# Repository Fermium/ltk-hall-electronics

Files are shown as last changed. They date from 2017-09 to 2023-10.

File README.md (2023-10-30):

# Free Open Scientific Equipment

Fermium LTD announces the free release of all scientific equipment designs under the terms of the MIT license. You are free to use them as you wish.

## Why?

Our small business is no longer competitive in this sector, and thus we've ceased production of this scientific equipment.

## What's Included

- Microwave Optics Kit:
  - [Microwave RX and TX](https://github.com/Fermium/ltk-mw-electronic): A pair of ultra-low-cost 10GHz microwave transmitters and receivers
  - [Microwave Kit Display](https://github.com/Fermium/frm-mw-display)
  - [Diode Detector](https://github.com/Fermium/frm-mw-diode-detector): A 10GHz diode detector for studying evanescent waves and wave propagation in waveguides
  - [Mechanics](https://github.com/Fermium/ltk-mw-mechanics) including:
    - [Transmitter and Receiver](https://github.com/Fermium/ltk-mw-mechanics/tree/master/transmitter%20and%20receiver) with rear protractor
    - [Structure](https://github.com/Fermium/ltk-mw-mechanics/tree/master/structure) with feet, rulers, center protractor, and center mount
    - [PCB Optics Components](https://github.com/Fermium/ltk-mw-mechanics/tree/master/pcbs): Mirrors, polarizers, photon-sieves, Fresnel zone plates
    - [Waveguides](https://github.com/Fermium/ltk-mw-mechanics/tree/master/accessories/waveguides)

- Hall Effect Apparatus:
  - [Electronics](https://github.com/Fermium/ltk-hall-electronics) for the 2015, 2017, and 2019 models
  - [2015 Firmware](https://github.com/Fermium/Hall-firmware)
  - [2017 Firmware](https://github.com/Fermium/hall-firmware-v2#hall-effect-apparatus-firmware---2017)

# Hall effect apparatus electronics

This repository contains the electronics for the Hall effect apparatus. The electronics are designed in Altium Designer.

The manual can be found [here](https://github.com/Fermium/hall-effect-handbook).

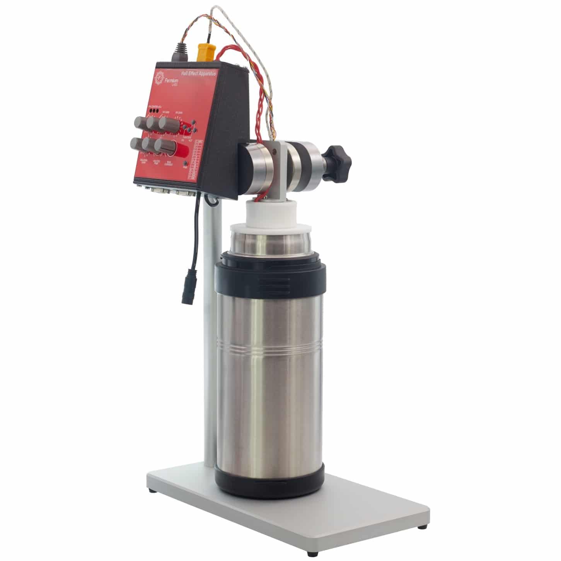
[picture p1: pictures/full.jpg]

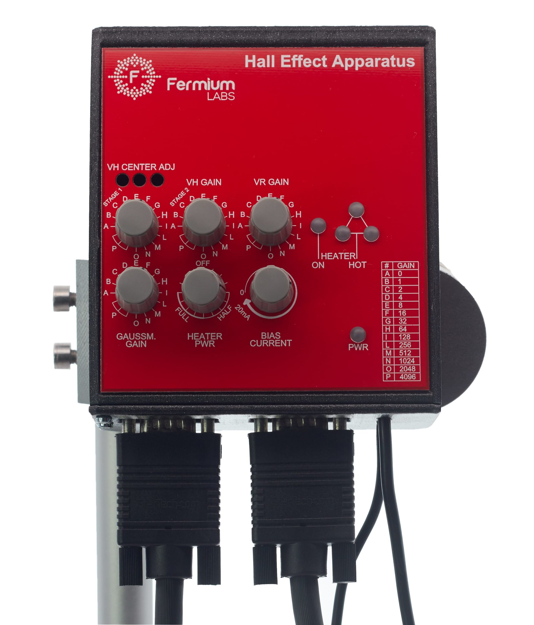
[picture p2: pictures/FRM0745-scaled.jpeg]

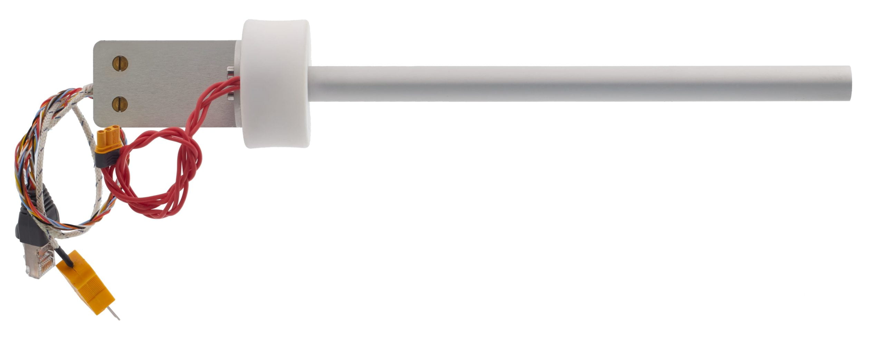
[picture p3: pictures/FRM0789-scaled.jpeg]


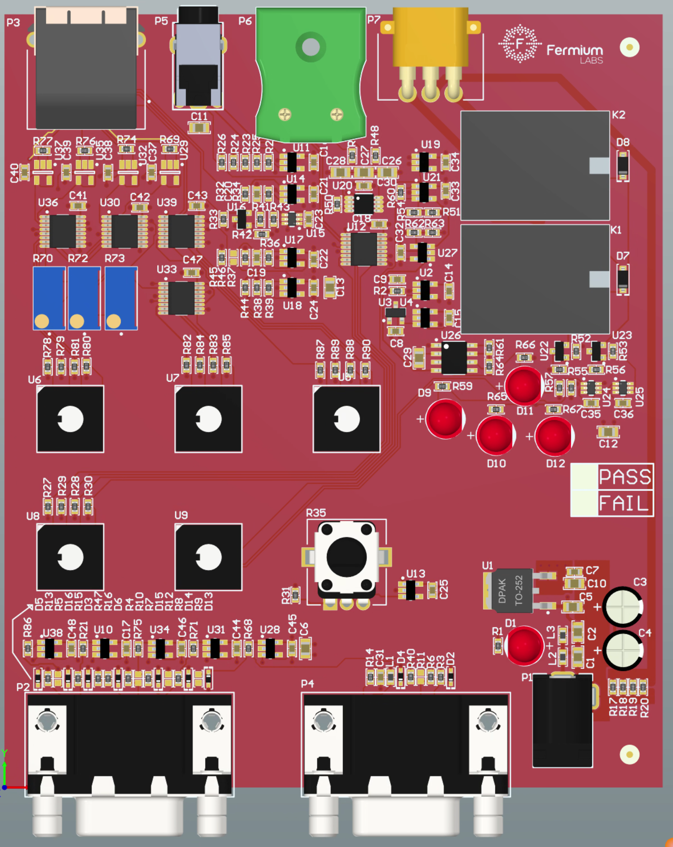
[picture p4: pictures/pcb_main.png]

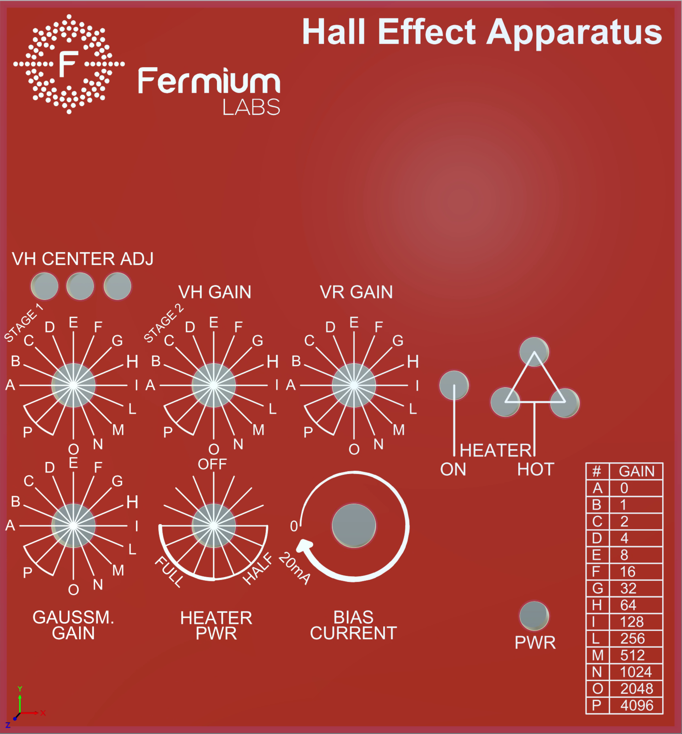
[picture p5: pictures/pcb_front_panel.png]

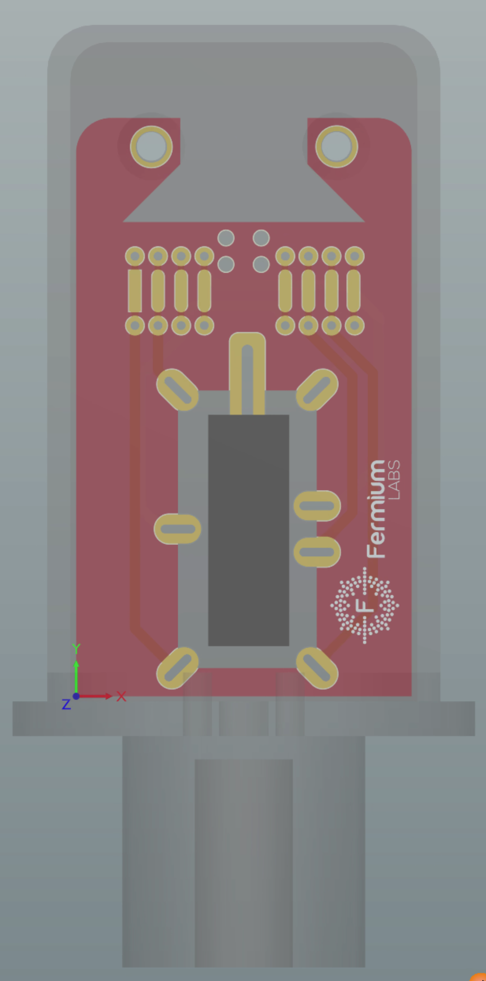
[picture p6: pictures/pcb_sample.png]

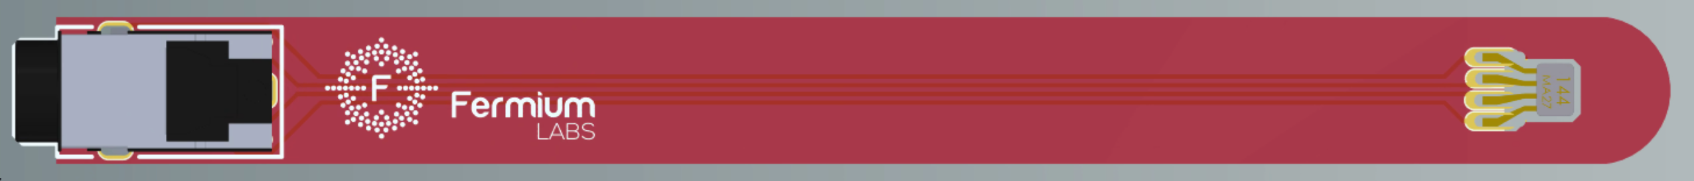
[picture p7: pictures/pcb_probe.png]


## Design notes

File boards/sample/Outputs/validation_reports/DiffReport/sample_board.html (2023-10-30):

Altium

# Differences Report for Project sample_board.PrjPcb and sample_board.PcbDoc

Date: | | 10/30/2023
Time: | | 4:42:38 PM
Filename: | | C:\Users\Shadow\Desktop\Repos\ltk-hall-electronics\exports\sample\validation_reports\DiffReport\sample_board.html

## Extra Room Definitions

Schematic Object | PCB Object
[Room sample_board (Scope=InComponentClass('sample_board')) TopLayer]

Back to top

## Different Comments

Schematic Object | PCB Object
Ge-P type [U1] | Sample [U1]

Back to top

## Different Types

Schematic Object | PCB Object
[logo] | [logo]
[P1] | [P1]

Back to top

## Changed Net Names

Schematic Object | PCB Object
[SAMPLE-I_N] | [NetP1_8]

Back to top

## Different Component Parameters

Schematic Object | PCB Object
[P1] | [P1]
[U1] | [U1]

Back to top

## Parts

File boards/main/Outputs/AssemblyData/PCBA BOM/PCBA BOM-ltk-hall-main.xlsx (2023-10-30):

Line # | Quantity | Bom Notes | Description | Designator | Layer | Manufacturer 1 | Manufacturer Part Number 1 | Manufacturer 2 | Manufacturer Part Number 2 | Manufacturer 3 | Manufacturer Part Number 3 | Manufacturer 4 | Manufacturer Part Number 4 | Manufacturer 5 | Manufacturer Part Number 5 | S 1 | SPN 1 | S 2 | SPN 2 | S 3 | SPN 3 | S 4 | SPN 4 | S 5 | SPN 5 | S 6 | SPN 6 | S 7 | SPN 7 | S 8 | SPN 8
1 | 2 |  | CAP THT ELEC 220uF 25V 20% | C3, C4 |  | Rubycon | 25PK220MEFC-6.3*11 |  |  |  |  |  |  |  |  | LCSC | C109337
2 | 2 |  | CAP SMD MLCC 10nF 50V 0603 X7R | C19, C20 |  | Yageo | CC0603KRX7R9BB103 | Samsung Electro-Mechanics | CL10B103KB8NFNC | Yageo | CC0603JRX7R9BB103 |  |  |  |  | LCSC | C307477 | LCSC | C100042
3 | 4 |  | CAP SMD MLCC 10uF 25V 0805 X5R | C26, C27, C28, C29 |  | Samsung Electro-Mechanics | CL21A106KAYNNNE | Murata | GRM21BR61E106KA73L |  |  |  |  |  |  | LCSC | C84416 | LCSC | C15850
4 | 8 |  | CAP SMD MLCC 22uF 25V 0805 X5R | C1, C2, C5, C6, C10, C11, C12, C13 |  | Samsung Electro-Mechanics | CL21A106KAYNNNE | Murata | GRM21BR61E106KA73L |  |  |  |  |  |  | LCSC | C84416 | LCSC | C15850
5 | 32 |  | CAP SMD MLCC 100nF 25V 0603 X7R | C7, C8, C9, C14, C15, C16, C17, C18, C21, C22, C23, C24, C25, C30, C31, C32, C33, C34, C35, C36, C37, C38, C39, C40, C41, C42, C43, C44, C45, C46, C47, C48 |  | Samsung Electro-Mechanics | CL10B104KA8NNNC | Yageo | CC0603KRX7R9BB104 |  |  |  |  |  |  | LCSC | C1590 | LCSC | C14663
6 | 1 |  | CONN DC 3 POLE 15A PCB MALE | P7 |  | Changzhou Amass Elec | MR30PW-M |  |  |  |  |  |  |  |  | TME | MR30PW-M
7 | 2 |  | CONN D-SUB HD 15POLES BLACK THT | P2, P4 |  | FCI | ICD15S13E4GV00LF |  |  |  |  |  |  |  |  | TME | ICD15S13E4GV00LF
8 | 1 |  | CONN JACK 3.5MM 4POLE THT | P5 |  | Cliff | FC68125 |  |  |  |  |  |  |  |  | TME | FC68125
9 | 1 |  | CONN RJ45 SHIELDED | P3 |  | TE Connectivity | 5555153-1 |  |  |  |  |  |  |  |  | LCSC | C125072
10 | 1 |  | CONN THERMOCOUPLE K-TYPE THT | P6 |  | Labfacility | IM-K-PCB |  |  |  |  |  |  |  |  | Farnell | 3810628
11 | 1 |  | CONN THT DC JACK 0.5A 30VDC 5Kcycles | P1 |  | HRO Electronics | DC-005A-20A |  |  |  |  |  |  |  |  | LCSC | C191049
12 | 5 |  | DIODE LED THT 5MM RED 200mcd | D1, D9, D10, D11, D12 |  | Everlight | 333-2SURD/S530-A3-L |  |  |  |  |  |  |  |  | LCSC | C99758
13 | 2 |  | DIODE SMD 100V 150mA 1.5Vf SOD-123 4148 | D7, D8 |  | MCC | 1N4148W-TP |  |  |  |  |  |  |  |  | LCSC | C77978
14 | 9 |  | DIODE SMD TVS 5V BIDIRECTIONAL SOD-523 | D2, D3, D4, D5, D6, D13, D14, D15, D16 |  | Born Semiconductor | PESD5V0S1BBN | Nexperia | PESD5V0S1BB,115 |  |  |  |  |  |  | LCSC | C314264 | LCSC | C97640
15 | 3 |  | FER SMD CHIP 0603 800mA 1K@100MHz 300mOhm | L1, L2, L3 |  | TDK | MPZ1608S102ATA00 |  |  |  |  |  |  |  |  | LCSC | C76814
16 | 3 |  | IC LOGIC PORT CONFIGURABLE AND, OR, NAND, NOR, XOR, BUFFER, NOT 8ns 74XX58 SC-70 | U15, U24, U25 |  | ON Semiconductor | NC7SZ58P6X | Texas Instruments | SN74LVC1G58DCKR |  |  |  |  |  |  | LCSC | C232804 | LCSC | C7842
17 | 19 |  | IC OPAMP 65uV 1pA RRIO 5V 80mA SOT-23-5 | U2, U4, U10, U11, U13, U14, U17, U18, U19, U21, U27, U28, U29, U31, U32, U34, U35, U37, U38 |  | Analog Devices | AD8605ARTZ |  |  |  |  |  |  |  |  | LCSC | C9641
18 | 5 |  | IC PGA G0-4094 SPI-PARALLEL 5V RRIO SSOP-16 | U12, U30, U33, U36, U39 |  | Analog Devices | LTC6915CGN#PBF |  |  |  |  |  |  |  |  | Mouser | 584-LTC6915CGN#PBF
19 | 1 |  | IC SMD LINEAR VOLTAGE REGULATOR 5V 500mA DPAK/TO-252 | U1 |  | ST Microelectronics | L78M05ABDT-TR |  |  |  |  |  |  |  |  | LCSC | C58069
20 | 1 |  | IC SMD TIMER NE555 SOIC-8 | U26 |  | Texas Instruments | NE555DR |  |  |  |  |  |  |  |  | LCSC | C7593
21 | 1 |  | IC THERMOCOUPLE AMPLIFIER MSOP-8 | U20 |  | Analog Devices | AD8495ARMZ-R7 |  |  |  |  |  |  |  |  | LCSC | C59658
22 | 1 |  | IC VOLTAGE REF SERIES 2.5V 75ppm 0.2% SOT-23 | U3 |  | Texas Instruments | REF3025AIDBZR |  |  |  |  |  |  |  |  | LCSC | C11334
23 | 3 |  | MOSFET N-CHANNEL LOGIC LEVEL 300mA 3ohm 60V ESD-PROT 2N7002K SOT-23 | U16, U22, U23 |  | ON Semiconductor | 2N7002KT1G | Vishay | 2N7002K-T1-GE3 | Diodes Inc. | 2N7002K-7 |  |  |  |  | LCSC | C81445 | LCSC | C116584 | LCSC | C85047
24 | 1 |  | POT 10K 20% SHAFT 6mmx7.4mm LIN | R35 |  | ALPS | RK09K1130A6S |  |  |  |  |  |  |  |  | LCSC | C209770
25 | 1 |  | POT TRIMMER LINEAR 10K 25TURNS VERT THT | R72 |  | Bourns | 3296W-1-103LF |  |  |  |  |  |  |  |  | LCSC | C34846
26 | 2 |  | POT TRIMMER LINEAR 50K 25TURNS VERT THT | R70, R73 |  | Bourns | 3296W-1-503LF |  |  |  |  |  |  |  |  | LCSC | C83686
27 | 2 |  | RELAY SPDT 10A 250VAC 12VDC SUBMINIATURE | K1, K2 |  | Omron | G5LE-14-DC12 |  |  |  |  |  |  |  |  | LCSC | C116964
28 | 24 |  | RES SMD 0 OHM 5% 1/10W 0603 | R4, R5, R6, R7, R8, R9, R10, R11, R12, R13, R14, R15, R16, R17, R18, R19, R20, R31, R32, R46, R69, R74, R76, R77 |  | Yageo | RC0603JR-070RL | Uniroyal | 0603WAF0000T5E |  |  |  |  |  |  | LCSC | C95177 | LCSC | C21189
29 | 6 |  | RES SMD 1K OHM 1% 1/10W 0603 | R2, R22, R25, R37, R38, R40 |  | Yageo | RC0603FR-071KL | Uniroyal | 0603WAF1001T5E |  |  |  |  |  |  | LCSC | C21190 | LCSC | C22548
30 | 1 |  | RES SMD 1M OHM 1% 1/10W 0603 | R50 |  | Yageo | RC0603FR-071ML | Uniroyal | 0603WAF1004T5E |  |  |  |  |  |  | LCSC | C105578 | LCSC | C22935
31 | 1 |  | RES SMD 1.2K OHM 1% 1/10W 0603 | R62 |  | Yageo | RC0603FR-071K2L | Uniroyal | 0603WAF1201T5E |  |  |  |  |  |  | LCSC | C114605 | LCSC | C22765
32 | 1 |  | RES SMD 1.5K OHM 1% 1/10W 0603 | R63 |  | Yageo | RC0603FR-071K5L | Uniroyal | 0603WAF1501T5E |  |  |  |  |  |  | LCSC | C22843 | LCSC | C114668
33 | 1 |  | RES SMD 3.3K OHM 1% 1/10W 0603 | R51 |  | Yageo | RC0603FR-073K3L | Uniroyal | 0603WAF3301T5E |  |  |  |  |  |  | LCSC | C108078 | LCSC | C22978
34 | 1 |  | RES SMD 5.6K OHM 1% 1/10W 0603 | R54 |  | Yageo | RC0603FR-075K6L | Uniroyal | 0603WAF5601T5E |  |  |  |  |  |  | LCSC | C23189 | LCSC | C114627
35 | 1 |  | RES SMD 10 OHM 0.1% 1/16W 25ppm 0603 | R45 |  | Uniroyal | TC0325B100JT5E | Viking Tech | AR03BTCX0100 |  |  |  |  |  |  | LCSC | C319923 | LCSC | C146565
36 | 29 |  | RES SMD 10K OHM 1% 1/10W 0603 | R27, R28, R29, R30, R33, R34, R36, R42, R43, R48, R49, R55, R56, R57, R58, R61, R64, R78, R79, R80, R81, R82, R83, R84, R85, R87, R88, R89, R90 |  | Yageo | RC0603FR-0710KL | Uniroyal | 0603WAF1002T5E |  |  |  |  |  |  | LCSC | C98220 | LCSC | C25804
37 | 1 |  | RES SMD 24K OHM 1% 1/10W 0603 | R39 |  | Yageo | RC0603FR-0724KL |  |  |  |  |  |  |  |  | LCSC | C137760
38 | 1 |  | RES SMD 39K OHM 1% 1/10W 0603 | R60 |  | Yageo | RC0603FR-0739KL | Uniroyal | 0603WAF3902T5E |  |  |  |  |  |  | LCSC | C23153 | LCSC | C163424
39 | 16 |  | RES SMD 100 OHM 1% 1/10W 0603 | R3, R21, R23, R24, R41, R44, R47, R52, R53, R65, R66, R67, R68, R71, R75, R86 |  | Yageo | RC0603FR-07100RL | Uniroyal | 0603WAF1000T5E |  |  |  |  |  |  | LCSC | C105588 | LCSC | C22775
40 | 2 |  | RES SMD 330 OHM 1% 1/10W 0603 | R1, R59 |  | Yageo | RC0603FR-07330RL | Uniroyal | 0603WAF3300T5E |  |  |  |  |  |  | LCSC | C105881 | LCSC | C23138
41 | 1 |  | RES SMD 499 OHM 1% 1/10W 0603 | R26 |  | Yageo | RC0603FR-07499RL | Uniroyal | 0603WAF4990T5E |  |  |  |  |  |  | LCSC | C23065
42 | 5 |  | SWITCH ROTARY HEX/BCD 16 POSITIONS | U5, U6, U7, U8, U9 |  | Omron | A6R-162RS |  |  |  |  |  |  |  |  | TME | A6R-162RS

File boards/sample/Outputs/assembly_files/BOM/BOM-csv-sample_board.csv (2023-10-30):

Supplier Part Number 1 | Quantity | Comment | Footprint | Supplier 1 | Pads | Designator
ge-p-sample | 1 | Ge-P type | Germanium Sample | Changsha Santech Materials | N/A | U1

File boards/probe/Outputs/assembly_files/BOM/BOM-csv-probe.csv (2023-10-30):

Supplier Part Number 1 | Quantity | Manufacturer Part Number | Comment | Footprint | Supplier 1 | Designator | Pads | Manufacturer
FC68125 | 1 | FC68125 |  | FC68125 | TME | P1 | 5 THT | CLIFF
HE144P | 1 | HE144P |  | HE144P-buried | Asensor | U1 | 4 THT | Asensor

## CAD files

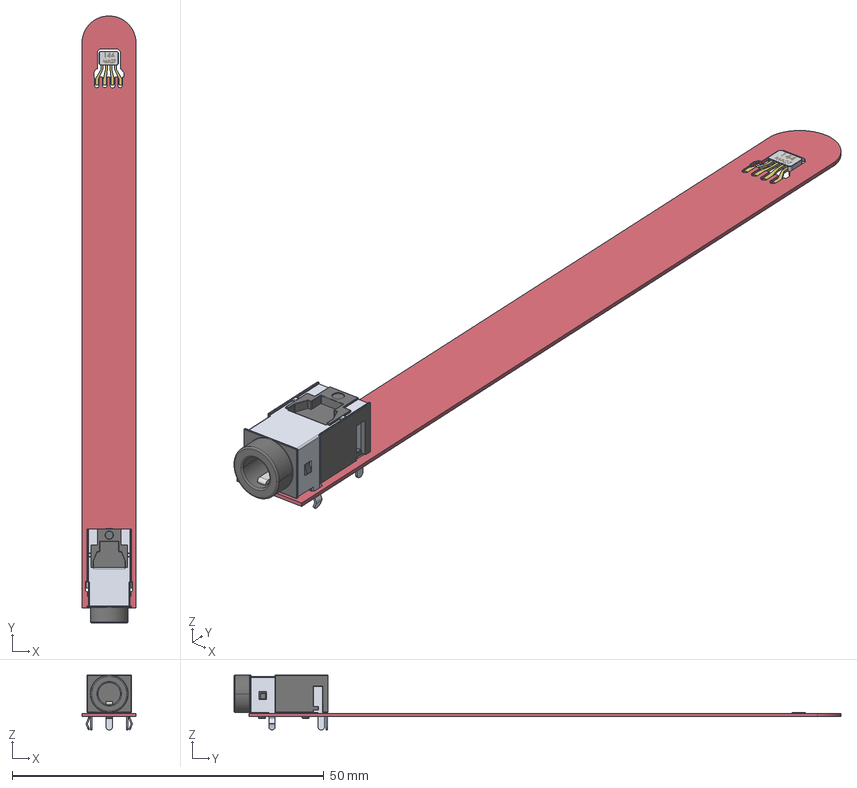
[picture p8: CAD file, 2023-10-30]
boards/probe/Outputs/assembly_files/ExportSTEP/probe.step
8.60 x 97.4 x 8.80 mm
short
FC68125

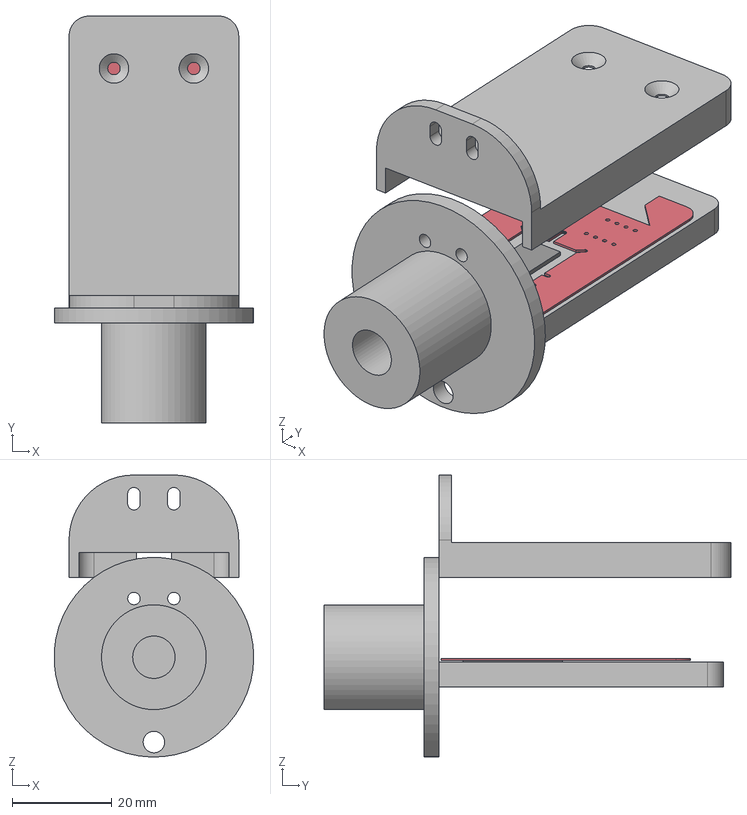
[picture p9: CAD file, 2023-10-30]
boards/sample/Outputs/assembly_files/ExportSTEP/sample_board.step
40.0 x 81.5 x 56.5 mm
Extruded
COPERCHIO_RGB8421504

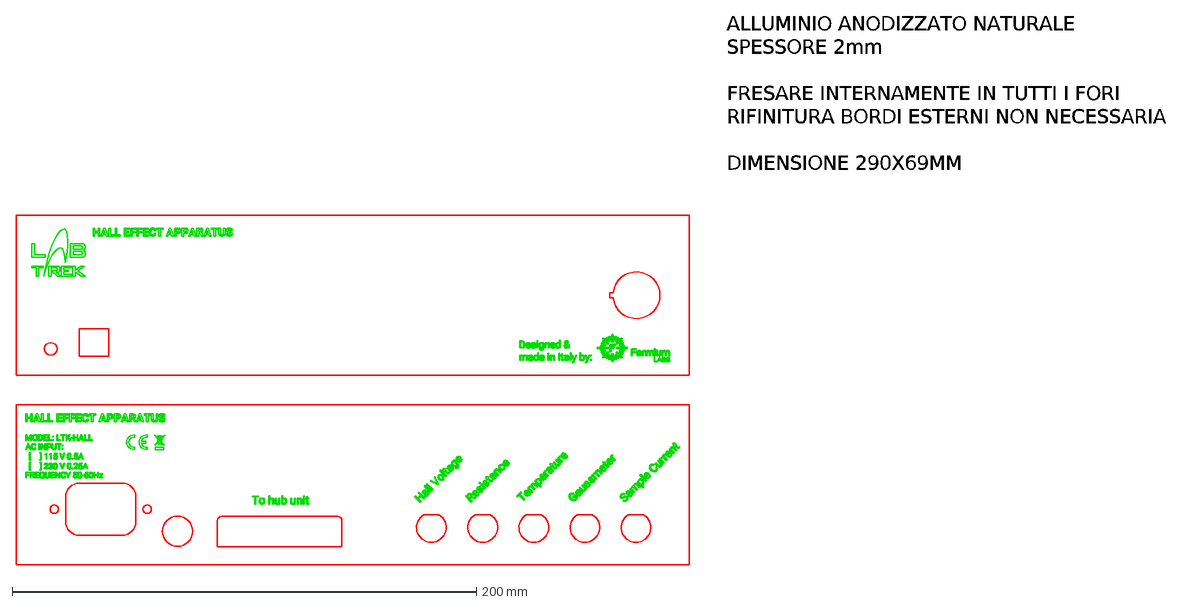
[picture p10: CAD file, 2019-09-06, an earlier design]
mechanical_OLD/front panels/main/main_definitivo_clean_dxf_2000.dxf
ALLUMINIO ANODIZZATO NATURALE SPESSORE 2mm FRESARE INTERNAMENTE IN TUTTI I FORI RIFINITURA BORDI ESTERNI NON NECESSARIA DIMENSIONE 290X69MM

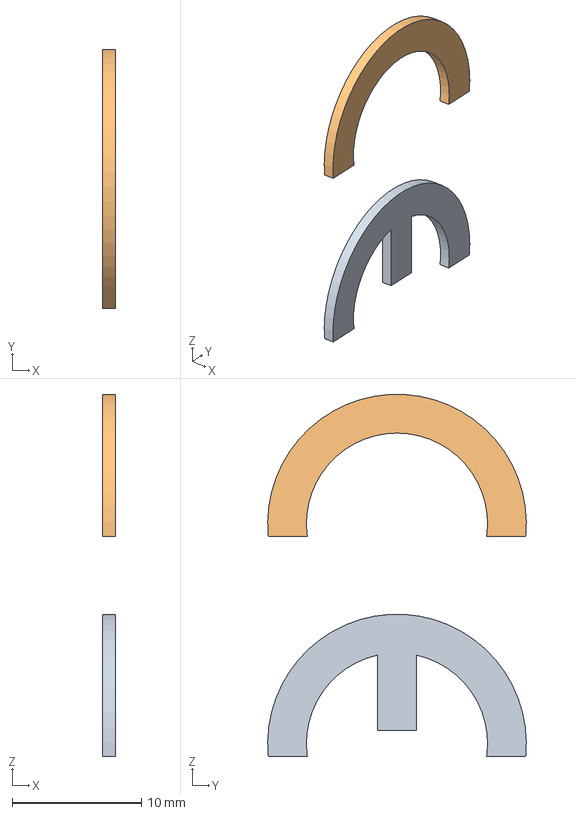
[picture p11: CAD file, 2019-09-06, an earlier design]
mechanical_OLD/front panels/components docs/ce-logo.snapshot.3/ce-logo.stp
1.00 x 20.0 x 28.0 mm

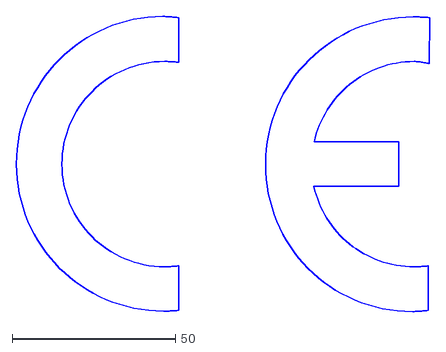
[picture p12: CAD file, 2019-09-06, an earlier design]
mechanical_OLD/front panels/components docs/CE_LOGO/CE_logo.dxf
126.5 x 90.3

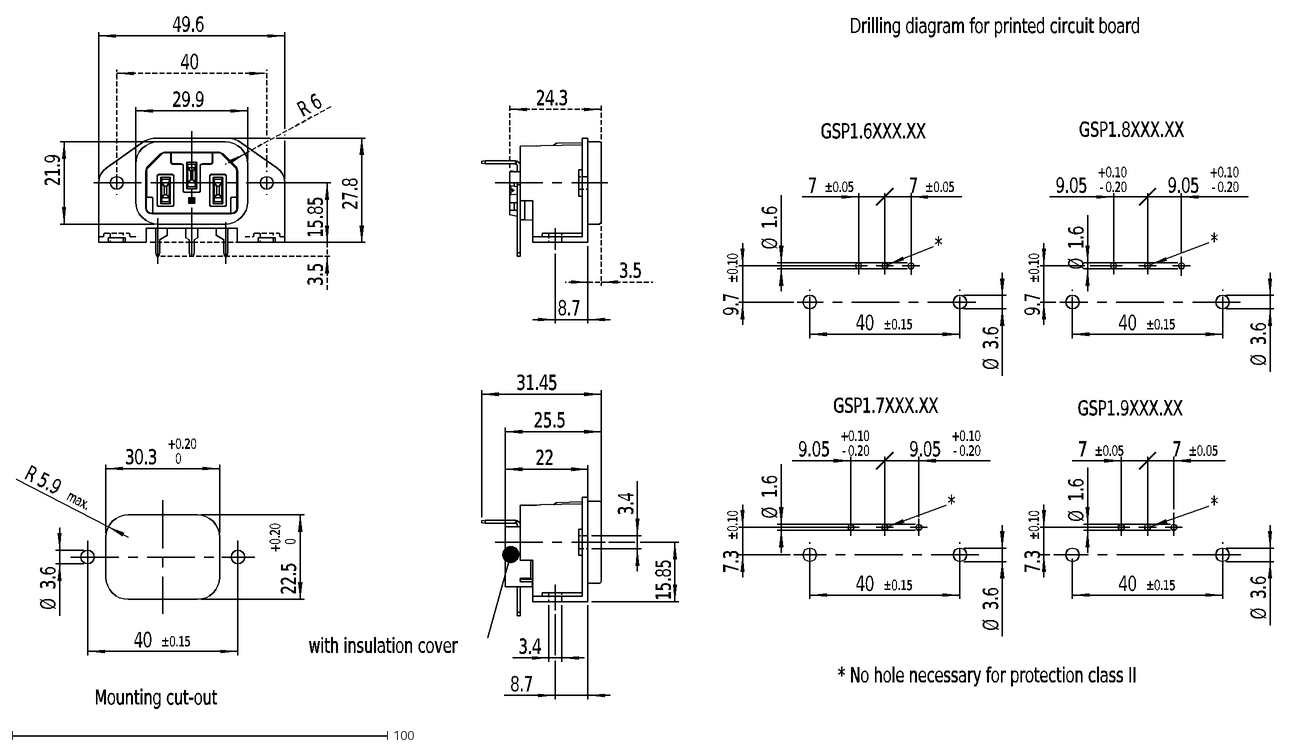
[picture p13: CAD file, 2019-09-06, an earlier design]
mechanical_OLD/front panels/components docs/e_0105.1305_2.1e001.dxf
3.5
15.85
29.9
21.9
27.8
49.6
40
R
6
8.7
24.3
25.5
22
31.45
3.4
with insulation cover
Ø
1.6
9.05
-
0.20
+
0.10
7
±0.05
7.3
±0.10
9.7
3.6
±0.15
Drilling diagram for printed circuit board
*
* No hole necessary for protection class II
GSP1.6XXX.XX
GSP1.7XXX.XX
GSP1.8XXX.XX
GSP1.9XXX.XX
30.3
0
22.5
5.9
max.
Mounting cut-out

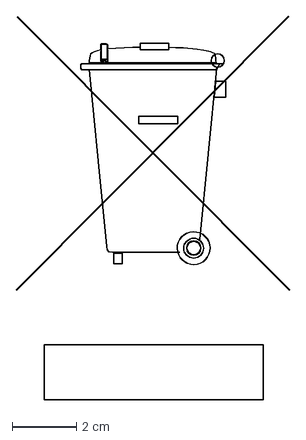
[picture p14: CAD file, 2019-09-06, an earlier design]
mechanical_OLD/front panels/components docs/WHEELIE_BIN_LOGO/Wheeled_bin.dxf
8.55 x 12.0 cm

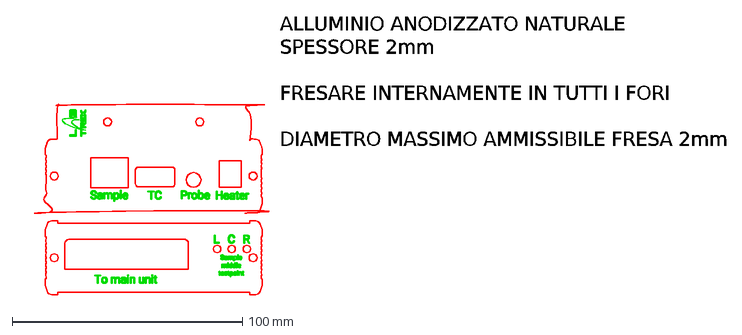
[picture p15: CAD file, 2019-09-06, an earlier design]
mechanical_OLD/front panels/hub/hub_definitivo_clean_dxf_2000.dxf
ALLUMINIO ANODIZZATO NATURALE SPESSORE 2mm FRESARE INTERNAMENTE IN TUTTI I FORI DIAMETRO MASSIMO AMMISSIBILE FRESA 2mm

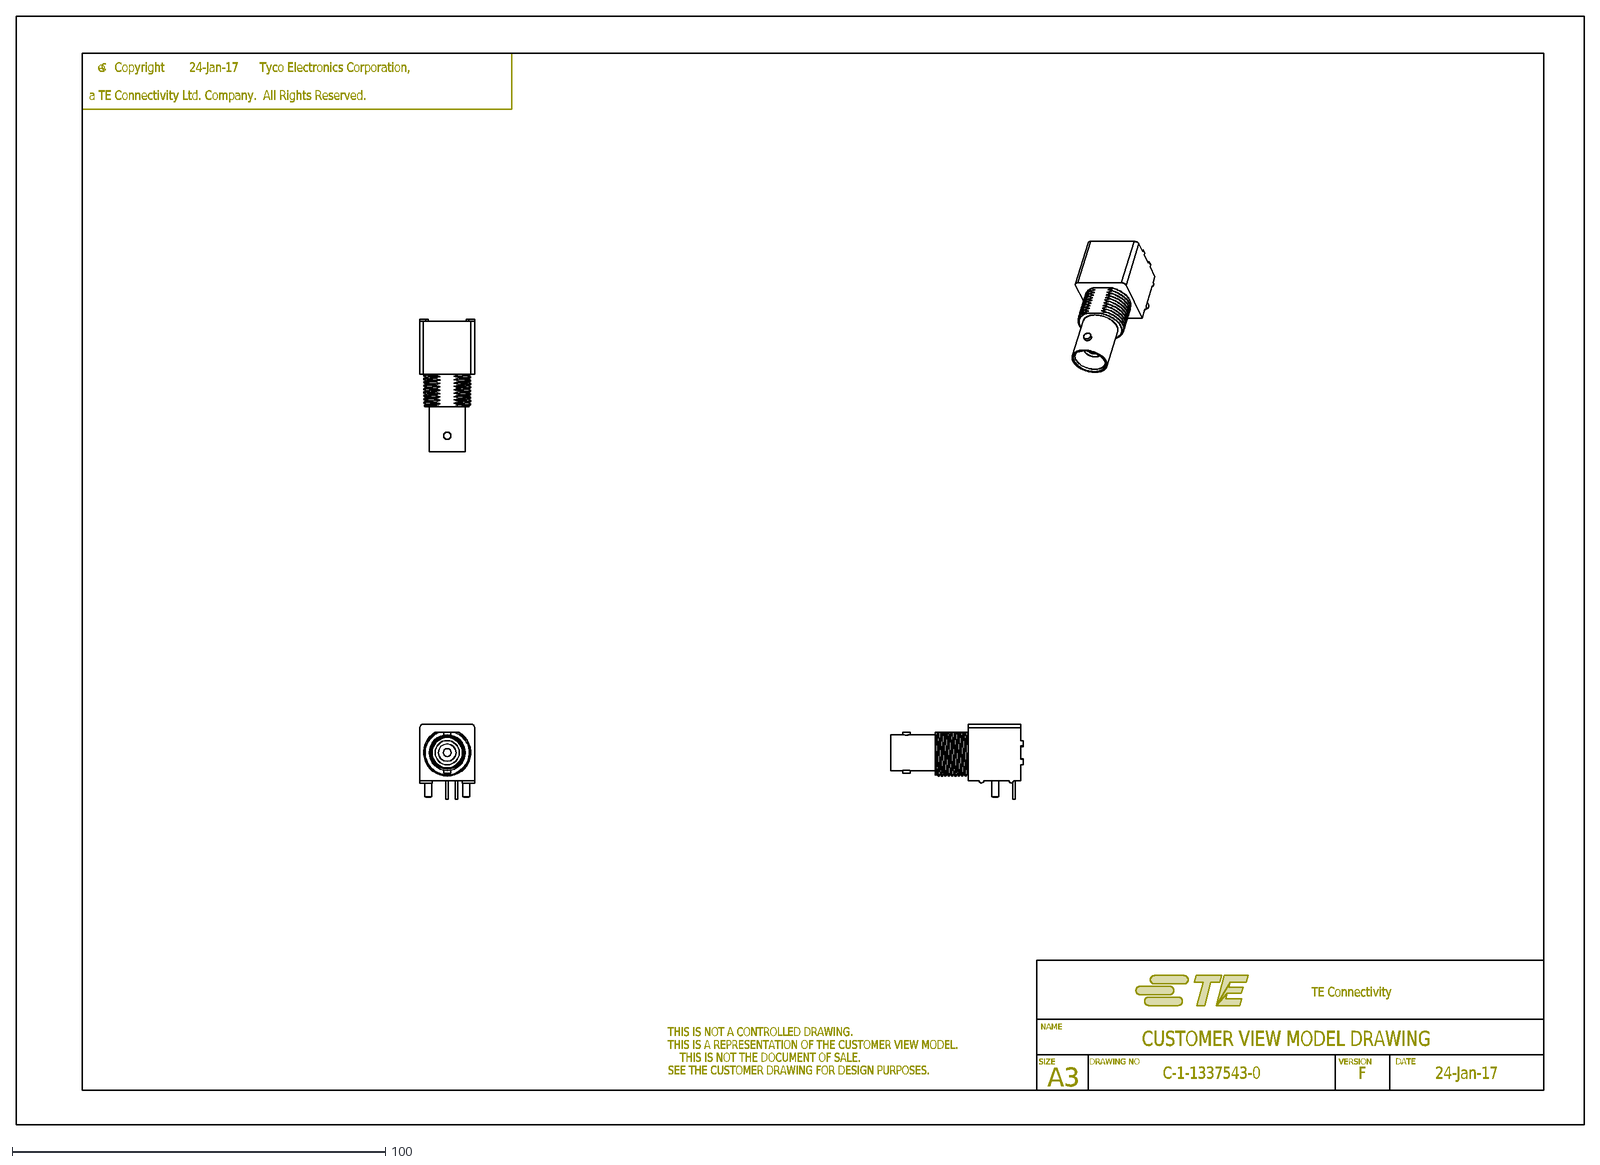
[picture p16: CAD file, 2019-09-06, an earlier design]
mechanical_OLD/front panels/components docs/c-1-1337543-0-f-2d.dxf
SIZE
DRAWING NO
VERSION
NAME
A3
CUSTOMER VIEW MODEL DRAWING
TE Connectivity
DATE
THIS IS NOT A CONTROLLED DRAWING.
THIS IS A REPRESENTATION OF THE CUSTOMER VIEW MODEL.
THIS IS NOT THE DOCUMENT OF SALE.
SEE THE CUSTOMER DRAWING FOR DESIGN PURPOSES.
c
C-1-1337543-0
F
24-Jan-17
Copyright
Tyco Electronics Corporation,
a TE Connectivity Ltd. Company. All Rights Reserved.

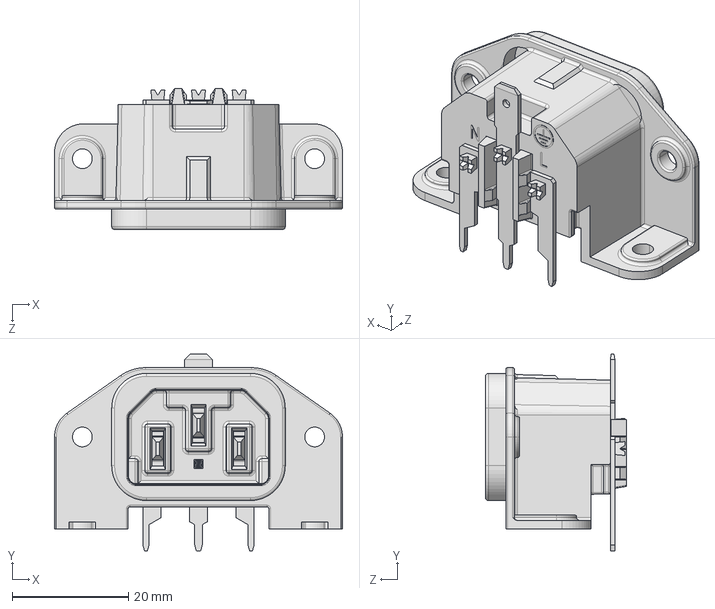
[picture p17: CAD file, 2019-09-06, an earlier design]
mechanical_OLD/front panels/components docs/e_0100.2041d007.step
49.6 x 33.9 x 24.3 mm

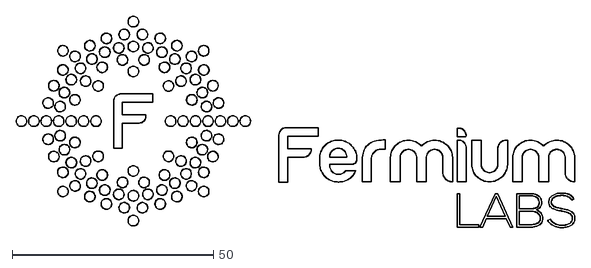
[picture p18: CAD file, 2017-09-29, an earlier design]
mechanical_OLD/front panels/components docs/Horizontal-Black.dxf
138.9 x 52.5

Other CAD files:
boards/main/Outputs/AssemblyData/AutoCAD dwg_dxf File PCB/ltk-hall-main.DWG
boards/main/Outputs/DevMechanicalData/ltk-hall-main.DWG
boards/probe/Outputs/assembly_files/AutoCAD PCB/probe.DWG
boards/sample/Outputs/assembly_files/AutoCAD PCB/sample_board.DWG
mechanical_OLD/front panels/main/main.dwg
mechanical_OLD/front panels/hub/Hub.dwg
mechanical_OLD/front panels/components docs/labtrek-logo.dwg
mechanical_OLD/front panels/components docs/Hub.dwg
mechanical_OLD/front panels/components docs/WHEELIE_BIN_LOGO/Wheeled_bin.dwg

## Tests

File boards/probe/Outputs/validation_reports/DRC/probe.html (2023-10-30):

Altium

# Design Rule Verification Report

Date: | | 10/30/2023
Time: | | 4:41:53 PM
Elapsed Time: | | 00:00:01
Filename: | | C:\Users\Shadow\Desktop\Repos\ltk-hall-electronics\boards\probe\probe.PcbDoc

Warnings: | | 0
Rule Violations: | | 34

## Summary

Warnings | Count
Total | 0

Rule Violations | Count
Clearance Constraint (Gap=6mil) (All),(All) | 12
Short-Circuit Constraint (Allowed=No) (All),(All) | 13
Un-Routed Net Constraint ( (All) ) | 0
Modified Polygon (Allow modified: No), (Allow shelved: No) | 0
Width Constraint (Min=6mil) (Max=200mil) (Preferred=10mil) (All) | 0
Power Plane Connect Rule(Relief Connect )(Expansion=20mil) (Conductor Width=10mil) (Air Gap=10mil) (Entries=4) (All) | 0
Hole Size Constraint (Min=11.811mil) (Max=100mil) (All) | 4
Hole To Hole Clearance (Gap=10mil) (All),(All) | 0
Minimum Solder Mask Sliver (Gap=10mil) (All),(All) | 3
Silk To Solder Mask (Clearance=10mil) (IsPad),(All) | 2
Silk to Silk (Clearance=10mil) (All),(All) | 0
Net Antennae (Tolerance=0mil) (All) | 0
Height Constraint (Min=0mil) (Max=1000mil) (Prefered=500mil) (All) | 0
Total | 34

Clearance Constraint (Gap=6mil) (All),(All)

Clearance Constraint: (Collision < 6mil) Between Board Cutout (Multi-Layer)Region (0 hole(s)) Multi-Layer And Pad U1-1(302.724mil,3542.307mil) on Multi-Layer

Clearance Constraint: (Collision < 6mil) Between Board Cutout (Multi-Layer)Region (0 hole(s)) Multi-Layer And Pad U1-1(302.724mil,3542.307mil) on Multi-Layer

Clearance Constraint: (Collision < 6mil) Between Board Cutout (Multi-Layer)Region (0 hole(s)) Multi-Layer And Pad U1-2(254.724mil,3541.307mil) on Multi-Layer

Clearance Constraint: (Collision < 6mil) Between Board Cutout (Multi-Layer)Region (0 hole(s)) Multi-Layer And Pad U1-2(254.724mil,3541.307mil) on Multi-Layer

Clearance Constraint: (Collision < 6mil) Between Board Cutout (Multi-Layer)Region (0 hole(s)) Multi-Layer And Pad U1-3(204.724mil,3543.307mil) on Multi-Layer

Clearance Constraint: (Collision < 6mil) Between Board Cutout (Multi-Layer)Region (0 hole(s)) Multi-Layer And Pad U1-3(204.724mil,3543.307mil) on Multi-Layer

Clearance Constraint: (Collision < 6mil) Between Board Cutout (Multi-Layer)Region (0 hole(s)) Multi-Layer And Pad U1-4(155.724mil,3542.307mil) on Multi-Layer

Clearance Constraint: (Collision < 6mil) Between Board Cutout (Multi-Layer)Region (0 hole(s)) Multi-Layer And Pad U1-4(155.724mil,3542.307mil) on Multi-Layer

Clearance Constraint: (Collision < 6mil) Between Board Cutout (Multi-Layer)Region (0 hole(s)) Multi-Layer And Track (157.48mil,3456.693mil)(157.48mil,3602.132mil) on Top Layer

Clearance Constraint: (Collision < 6mil) Between Board Cutout (Multi-Layer)Region (0 hole(s)) Multi-Layer And Track (157.48mil,3456.693mil)(157.48mil,3602.132mil) on Top Layer

Clearance Constraint: (Collision < 6mil) Between Board Cutout (Multi-Layer)Region (0 hole(s)) Multi-Layer And Track (303.15mil,3456.693mil)(303.15mil,3598.95mil) on Top Layer

Clearance Constraint: (Collision < 6mil) Between Board Cutout (Multi-Layer)Region (0 hole(s)) Multi-Layer And Track (303.15mil,3456.693mil)(303.15mil,3598.95mil) on Top Layer

Back to top

Short-Circuit Constraint (Allowed=No) (All),(All)

Short-Circuit Constraint: Between Board Cutout (Multi-Layer)Region (0 hole(s)) Multi-Layer And Board Cutout (Multi-Layer)Region (0 hole(s)) Multi-Layer Location : [X = 4680.685mil][Y = 5609.394mil]

Short-Circuit Constraint: Between Board Cutout (Multi-Layer)Region (0 hole(s)) Multi-Layer And Pad U1-1(302.724mil,3542.307mil) on Multi-Layer Location : [X = 4751.543mil][Y = 5545.398mil]

Short-Circuit Constraint: Between Board Cutout (Multi-Layer)Region (0 hole(s)) Multi-Layer And Pad U1-1(302.724mil,3542.307mil) on Multi-Layer Location : [X = 4751.543mil][Y = 5545.398mil]

Short-Circuit Constraint: Between Board Cutout (Multi-Layer)Region (0 hole(s)) Multi-Layer And Pad U1-2(254.724mil,3541.307mil) on Multi-Layer Location : [X = 4703.543mil][Y = 5544.874mil]

Short-Circuit Constraint: Between Board Cutout (Multi-Layer)Region (0 hole(s)) Multi-Layer And Pad U1-2(254.724mil,3541.307mil) on Multi-Layer Location : [X = 4703.543mil][Y = 5544.874mil]

Short-Circuit Constraint: Between Board Cutout (Multi-Layer)Region (0 hole(s)) Multi-Layer And Pad U1-3(204.724mil,3543.307mil) on Multi-Layer Location : [X = 4653.543mil][Y = 5545.874mil]

Short-Circuit Constraint: Between Board Cutout (Multi-Layer)Region (0 hole(s)) Multi-Layer And Pad U1-3(204.724mil,3543.307mil) on Multi-Layer Location : [X = 4653.543mil][Y = 5545.874mil]

Short-Circuit Constraint: Between Board Cutout (Multi-Layer)Region (0 hole(s)) Multi-Layer And Pad U1-4(155.724mil,3542.307mil) on Multi-Layer Location : [X = 4605.083mil][Y = 5545.214mil]

Short-Circuit Constraint: Between Board Cutout (Multi-Layer)Region (0 hole(s)) Multi-Layer And Pad U1-4(155.724mil,3542.307mil) on Multi-Layer Location : [X = 4605.083mil][Y = 5545.224mil]

Short-Circuit Constraint: Between Board Cutout (Multi-Layer)Region (0 hole(s)) Multi-Layer And Track (157.48mil,3456.693mil)(157.48mil,3602.132mil) on Top Layer Location : [X = 4606.299mil][Y = 5546.96mil]

Short-Circuit Constraint: Between Board Cutout (Multi-Layer)Region (0 hole(s)) Multi-Layer And Track (157.48mil,3456.693mil)(157.48mil,3602.132mil) on Top Layer Location : [X = 4606.299mil][Y = 5548.001mil]

Short-Circuit Constraint: Between Board Cutout (Multi-Layer)Region (0 hole(s)) Multi-Layer And Track (303.15mil,3456.693mil)(303.15mil,3598.95mil) on Top Layer Location : [X = 4751.968mil][Y = 5546.597mil]

Short-Circuit Constraint: Between Board Cutout (Multi-Layer)Region (0 hole(s)) Multi-Layer And Track (303.15mil,3456.693mil)(303.15mil,3598.95mil) on Top Layer Location : [X = 4751.968mil][Y = 5546.682mil]

Back to top

Hole Size Constraint (Min=11.811mil) (Max=100mil) (All)

Hole Size Constraint: (118.11mil > 100mil) Pad U1-1(302.724mil,3542.307mil) on Multi-Layer Actual Slot Hole Width = 118.11mil

Hole Size Constraint: (118.11mil > 100mil) Pad U1-2(254.724mil,3541.307mil) on Multi-Layer Actual Slot Hole Width = 118.11mil

Hole Size Constraint: (118.11mil > 100mil) Pad U1-3(204.724mil,3543.307mil) on Multi-Layer Actual Slot Hole Width = 118.11mil

Hole Size Constraint: (118.11mil > 100mil) Pad U1-4(155.724mil,3542.307mil) on Multi-Layer Actual Slot Hole Width = 118.11mil

Back to top

Minimum Solder Mask Sliver (Gap=10mil) (All),(All)

Minimum Solder Mask Sliver Constraint: (0.63mil < 10mil) Between Pad U1-1(302.724mil,3542.307mil) on Multi-Layer And Pad U1-2(254.724mil,3541.307mil) on Multi-Layer [Top Solder] Mask Sliver [0.63mil] / [Bottom Solder] Mask Sliver [0.63mil]

Minimum Solder Mask Sliver Constraint: (2.63mil < 10mil) Between Pad U1-2(254.724mil,3541.307mil) on Multi-Layer And Pad U1-3(204.724mil,3543.307mil) on Multi-Layer [Top Solder] Mask Sliver [2.63mil] / [Bottom Solder] Mask Sliver [2.63mil]

Minimum Solder Mask Sliver Constraint: (1.63mil < 10mil) Between Pad U1-3(204.724mil,3543.307mil) on Multi-Layer And Pad U1-4(155.724mil,3542.307mil) on Multi-Layer [Top Solder] Mask Sliver [1.63mil] / [Bottom Solder] Mask Sliver [1.63mil]

Back to top

Silk To Solder Mask (Clearance=10mil) (IsPad),(All)

Silk To Solder Mask Clearance Constraint: (8.296mil < 10mil) Between Pad P1-1(232.425mil,686.646mil) on Multi-Layer And Track (85.425mil,719.646mil)(385.425mil,719.646mil) on Top Overlay [Top Overlay] to [Top Solder] clearance [8.296mil]

Silk To Solder Mask Clearance Constraint: (9.296mil < 10mil) Between Pad P1-2(119.425mil,655.646mil) on Multi-Layer And Track (85.425mil,389.646mil)(85.425mil,719.646mil) on Top Overlay [Top Overlay] to [Top Solder] clearance [9.296mil]

Back to top

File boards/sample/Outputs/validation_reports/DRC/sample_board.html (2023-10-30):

Altium

# Design Rule Verification Report

Date: | | 10/30/2023
Time: | | 4:42:36 PM
Elapsed Time: | | 00:00:01
Filename: | | C:\Users\Shadow\Desktop\Repos\ltk-hall-electronics\boards\sample\sample_board.PcbDoc

Warnings: | | 0
Rule Violations: | | 6

## Summary

Warnings | Count
Total | 0

Rule Violations | Count
Clearance Constraint (Gap=10mil) (Disabled)(All),(All) | 0
Short-Circuit Constraint (Allowed=No) (Disabled)(All),(All) | 0
Un-Routed Net Constraint ( (All) ) | 6
Modified Polygon (Allow modified: No), (Allow shelved: No) | 0
Width Constraint (Min=10mil) (Max=50mil) (Preferred=25mil) (All) | 0
Power Plane Connect Rule(Relief Connect )(Expansion=20mil) (Conductor Width=10mil) (Air Gap=10mil) (Entries=4) (All) | 0
Hole Size Constraint (Min=1mil) (Max=100mil) (Disabled)(All) | 0
Hole To Hole Clearance (Gap=10mil) (Disabled)(All),(All) | 0
Minimum Solder Mask Sliver (Gap=10mil) (All),(All) | 0
Silk To Solder Mask (Clearance=10mil) (Disabled)(All),(All) | 0
Silk to Silk (Clearance=10mil) (All),(All) | 0
Net Antennae (Tolerance=0mil) (All) | 0
Height Constraint (Min=0mil) (Max=1000mil) (Prefered=500mil) (All) | 0
Silk primitive without silk layer | 0
Total | 6

Un-Routed Net Constraint ( (All) )

Un-Routed Net Constraint: Via (256mil,1870.001mil) from Top Layer to Bottom Layer Dead Copper - Net Not Assigned.

Un-Routed Net Constraint: Via (510mil,1470mil) from Top Layer to Bottom Layer Dead Copper - Net Not Assigned.

Un-Routed Net Constraint: Via (510mil,1560mil) from Top Layer to Bottom Layer Dead Copper - Net Not Assigned.

Un-Routed Net Constraint: Via (630mil,1470mil) from Top Layer to Bottom Layer Dead Copper - Net Not Assigned.

Un-Routed Net Constraint: Via (630mil,1560mil) from Top Layer to Bottom Layer Dead Copper - Net Not Assigned.

Un-Routed Net Constraint: Via (887mil,1871.001mil) from Top Layer to Bottom Layer Dead Copper - Net Not Assigned.

Back to top

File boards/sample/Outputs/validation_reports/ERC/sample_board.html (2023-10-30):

Altium

# Electrical Rule Check Report

Date: | | 10/30/2023
Time: | | 4:42:35 PM
Filename: | | C:\Users\Shadow\Desktop\Repos\ltk-hall-electronics\exports\sample\validation_reports\ERC\sample_board.html

Class | Document | Message
Warning | sample_board.SchDoc | Nets Wire SAMPLE-VH1_P has multiple names (Net Label SAMPLE-VH1_P, Net Label SAMPLE-VH2_P)
Warning | sample_board.SchDoc | Off grid Net Label SAMPLE-I_P at 4841.509mil,4150mil
Warning | sample_board.SchDoc | Off grid Net Label SAMPLE-VH1_P at 4696.006mil,4550mil
Warning | sample_board.SchDoc | Off grid Net Label SAMPLE-VH2_N at 4678.671mil,4250mil
Warning | sample_board.SchDoc | Off grid Net Label SAMPLE-Vr_N at 4758.962mil,4650mil
Warning | sample_board.SchDoc | Off grid Net Label SAMPLE-Vr_P at 4776.297mil,4750mil

Back to top

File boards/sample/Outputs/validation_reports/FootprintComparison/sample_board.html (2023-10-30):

Altium customize

# Footprint Comparison Report

Date: | | 10/30/2023
Time: | | 4:42:37 PM
Elapsed Time: | | 00:00:00
Filename: | | C:\Users\Shadow\Desktop\Repos\ltk-hall-electronics\boards\sample\sample_board.PcbDoc

## Contents

Contents

Components Status Summary

Footprints Not Found

## Components Status Summary

## Footprints Not Found

Designator | Footprint | Library to install
logo | frm-med | custom_components.PcbLib
P1 | Edge Connector | custom_components.PcbLib
U1 | GERMANIUM SAMPLE | germanium.PcbLib

Back to top

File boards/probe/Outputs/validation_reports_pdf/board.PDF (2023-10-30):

## Electrical Rules Check Report

Class | Document | Message Successful Compile for probe.PrjPcb
Monday 30 Oct 2023 4:41:44 PM | Page 1 of 1

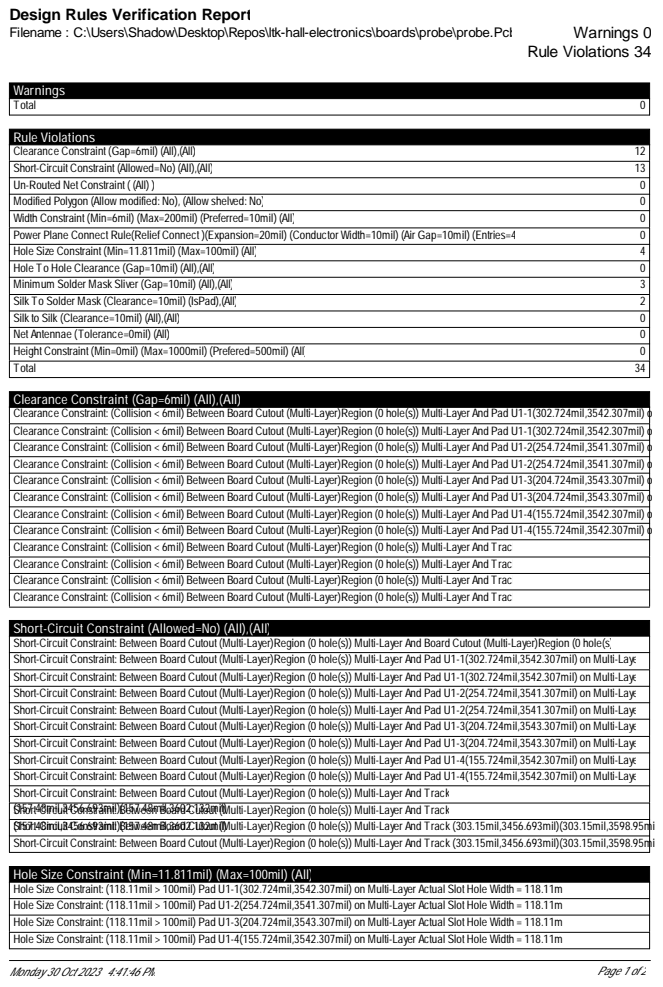
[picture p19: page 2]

Design Rules Verification Report

Clearance Constraint (Gap=6mil) (All),(All)
Clearance Constraint: (Collision < 6mil) Between Board Cutout (Multi-Layer)Region (0 hole(s)) Multi-Layer And Pad U1-1(302.724mil,3542.307mil) o
Clearance Constraint: (Collision < 6mil) Between Board Cutout (Multi-Layer)Region (0 hole(s)) Multi-Layer And Pad U1-2(254.724mil,3541.307mil) o
Clearance Constraint: (Collision < 6mil) Between Board Cutout (Multi-Layer)Region (0 hole(s)) Multi-Layer And Pad U1-3(204.724mil,3543.307mil) o
Clearance Constraint: (Collision < 6mil) Between Board Cutout (Multi-Layer)Region (0 hole(s)) Multi-Layer And Pad U1-4(155.724mil,3542.307mil) o
Clearance Constraint: (Collision < 6mil) Between Board Cutout (Multi-Layer)Region (0 hole(s)) Multi-Layer And Trac

Short-Circuit Constraint (Allowed=No) (All),(All)
Short-Circuit Constraint: Between Board Cutout (Multi-Layer)Region (0 hole(s)) Multi-Layer And Board Cutout (Multi-Layer)Region (0 hole(s))
Short-Circuit Constraint: Between Board Cutout (Multi-Layer)Region (0 hole(s)) Multi-Layer And Pad U1-1(302.724mil,3542.307mil) on Multi-Laye
Short-Circuit Constraint: Between Board Cutout (Multi-Layer)Region (0 hole(s)) Multi-Layer And Pad U1-2(254.724mil,3541.307mil) on Multi-Laye
Short-Circuit Constraint: Between Board Cutout (Multi-Layer)Region (0 hole(s)) Multi-Layer And Pad U1-3(204.724mil,3543.307mil) on Multi-Laye
Short-Circuit Constraint: Between Board Cutout (Multi-Layer)Region (0 hole(s)) Multi-Layer And Pad U1-4(155.724mil,3542.307mil) on Multi-Laye
Short-Circuit Constraint: Between Board Cutout (Multi-Layer)Region (0 hole(s)) Multi-Layer And Track
(1Sh5o7rt.4-Ci 8mrcil
Short-Circuit Constraint: Between Board Cutout (Multi-Layer)Region (0 hole(s)) Multi-Layer And Track (303.15mil,3456.693mil)(303.15mil,3598.95mi

u,3it4Co56n.6st9ra3mint
u,3it4Co56n.6st9ra3minti:l)(1Be5twe7.4e8nmBilo,3a6rd02Cu.13to2umt (Mil) ulti-Layer)Region (0 hole(s)) Multi-Layer And Track (303.15mil,3456.693mil)(303.15mil,3598.95mi

o,3a6rd02Cu.13to2umt (Mil) ulti-Layer)Region (0 hole(s)) Multi-Layer And Track

Hole Size Constraint (Min=11.811mil) (Max=100mil) (All)
Hole Size Constraint: (118.11mil > 100mil) Pad U1-1(302.724mil,3542.307mil) on Multi-Layer Actual Slot Hole Width = 118.11m
Hole Size Constraint: (118.11mil > 100mil) Pad U1-2(254.724mil,3541.307mil) on Multi-Layer Actual Slot Hole Width = 118.11m
Hole Size Constraint: (118.11mil > 100mil) Pad U1-3(204.724mil,3543.307mil) on Multi-Layer Actual Slot Hole Width = 118.11m
Hole Size Constraint: (118.11mil > 100mil) Pad U1-4(155.724mil,3542.307mil) on Multi-Layer Actual Slot Hole Width = 118.11m

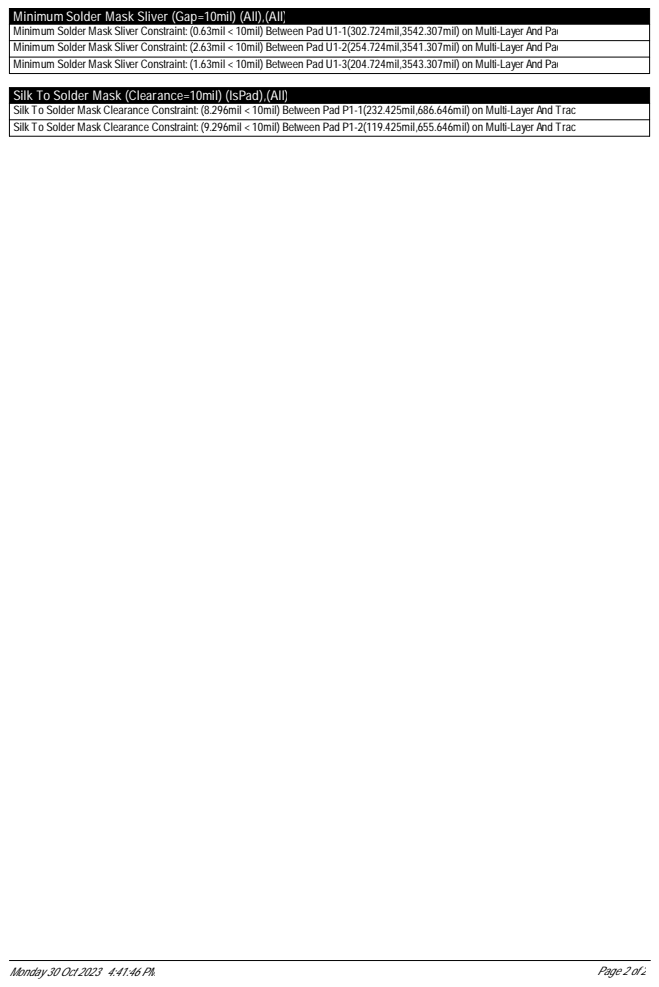
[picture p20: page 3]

Minimum Solder Mask Sliver (Gap=10mil) (All),(All)
Minimum Solder Mask Sliver Constraint: (0.63mil < 10mil) Between Pad U1-1(302.724mil,3542.307mil) on Multi-Layer And Pad
Minimum Solder Mask Sliver Constraint: (2.63mil < 10mil) Between Pad U1-2(254.724mil,3541.307mil) on Multi-Layer And Pad
Minimum Solder Mask Sliver Constraint: (1.63mil < 10mil) Between Pad U1-3(204.724mil,3543.307mil) on Multi-Layer And Pad

Silk To Solder Mask (Clearance=10mil) (IsPad),(All)
Silk To Solder Mask Clearance Constraint: (8.296mil < 10mil) Between Pad P1-1(232.425mil,686.646mil) on Multi-Layer And Trac
Silk To Solder Mask Clearance Constraint: (9.296mil < 10mil) Between Pad P1-2(119.425mil,655.646mil) on Multi-Layer And Trac

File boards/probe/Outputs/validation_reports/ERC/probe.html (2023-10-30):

Altium

# Electrical Rule Check Report

Date: | | 10/30/2023
Time: | | 4:41:53 PM
Filename: | | C:\Users\Shadow\Desktop\Repos\ltk-hall-electronics\exports\probe\validation_reports\ERC\probe.html

Class | Document | Message

Successful Compile; No Violations Found.

Back to top

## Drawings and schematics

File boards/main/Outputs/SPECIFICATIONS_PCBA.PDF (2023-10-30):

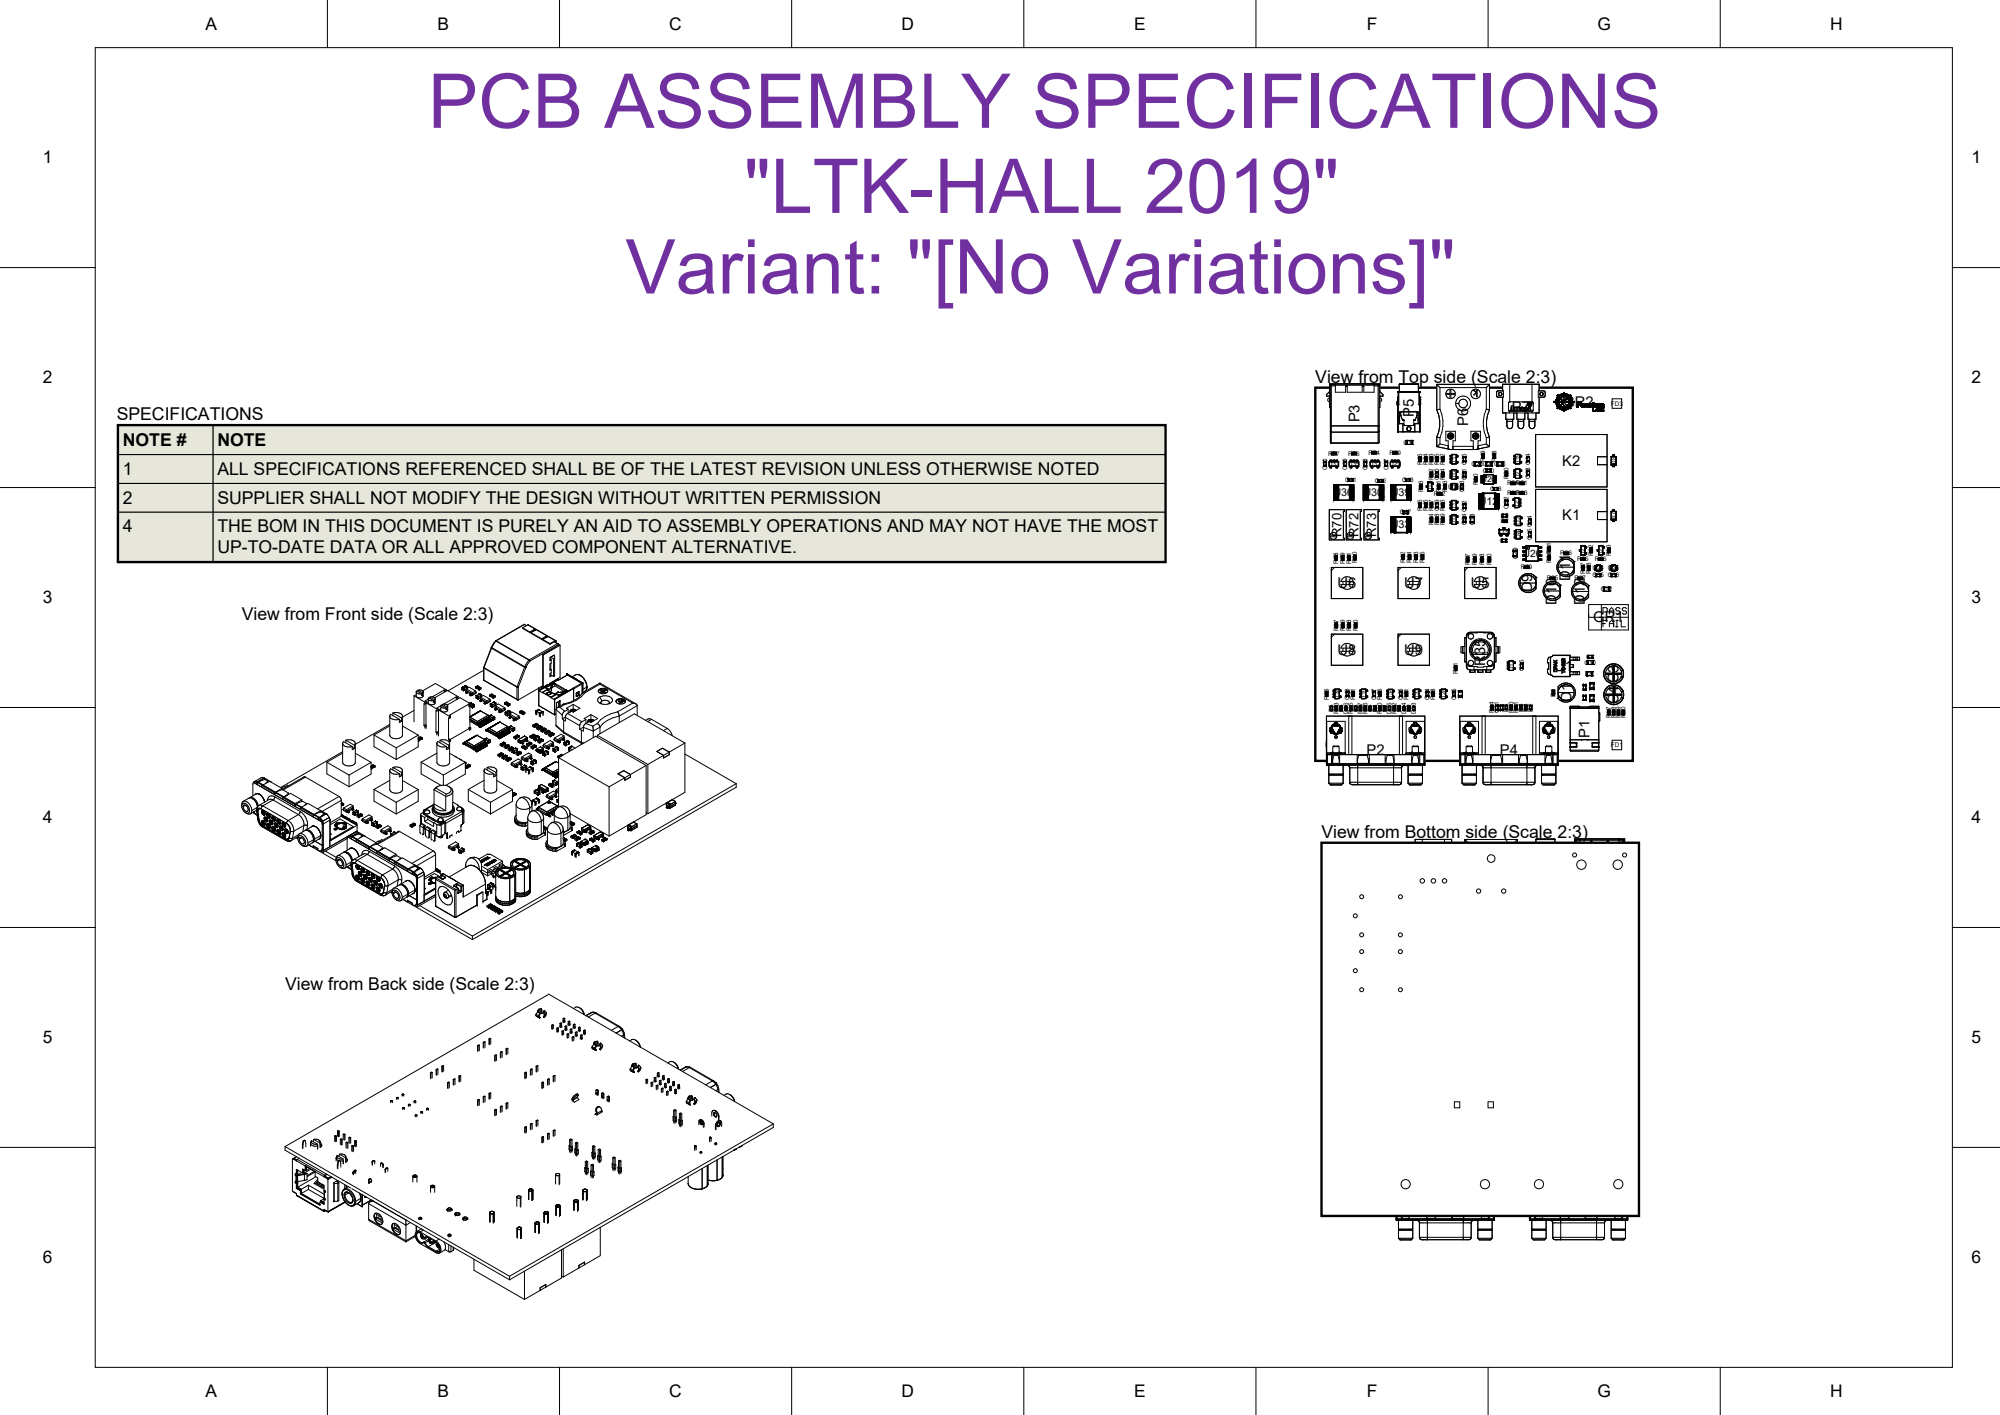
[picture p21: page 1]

View from Top side (Scale 2:3)

NOTE
ALL SPECIFICATIONS REFERENCED SHALL BE OF THE LATEST REVISION UNLESS OTHERWISE NOTED

SUPPLIER SHALL NOT MODIFY THE DESIGN WITHOUT WRITTEN PERMISSION
THE BOM IN THIS DOCUMENT IS PURELY AN AID TO ASSEMBLY OPERATIONS AND MAY NOT HAVE THE MOST
UP-TO-DATE DATA OR ALL APPROVED COMPONENT ALTERNATIVE.

View from Front side (Scale 2:3)

View from Bottom side (Scale 2:3)

View from Back side (Scale 2:3)

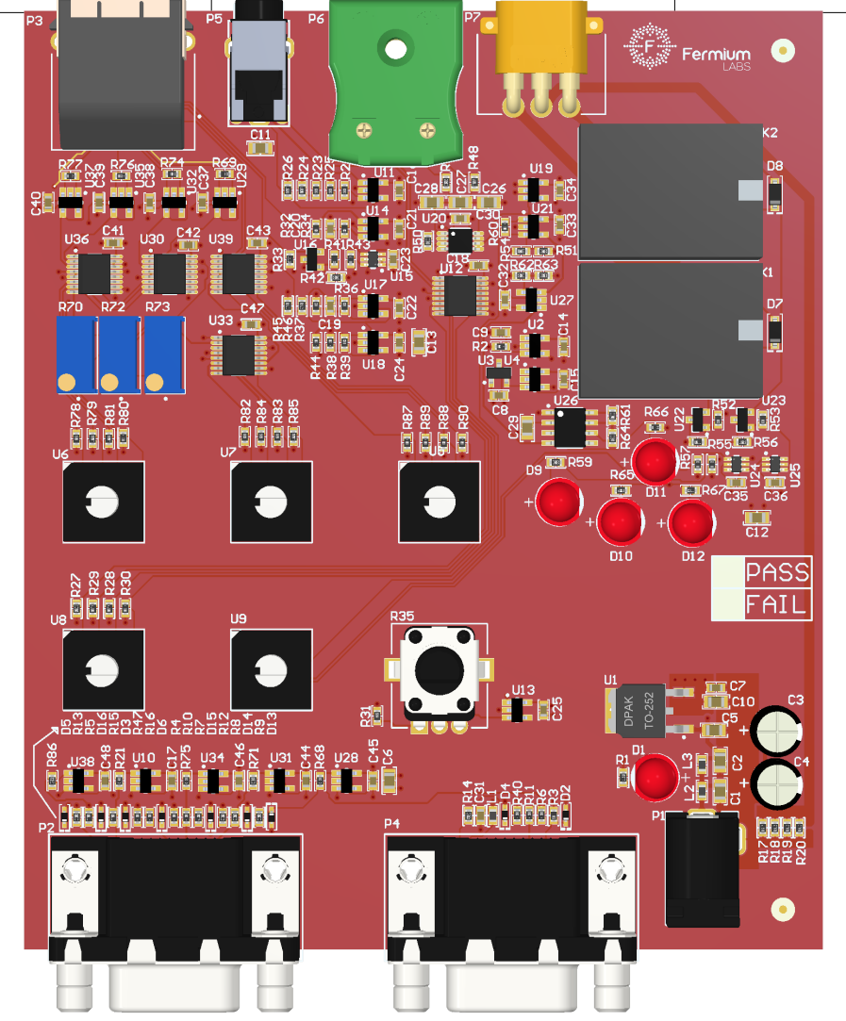
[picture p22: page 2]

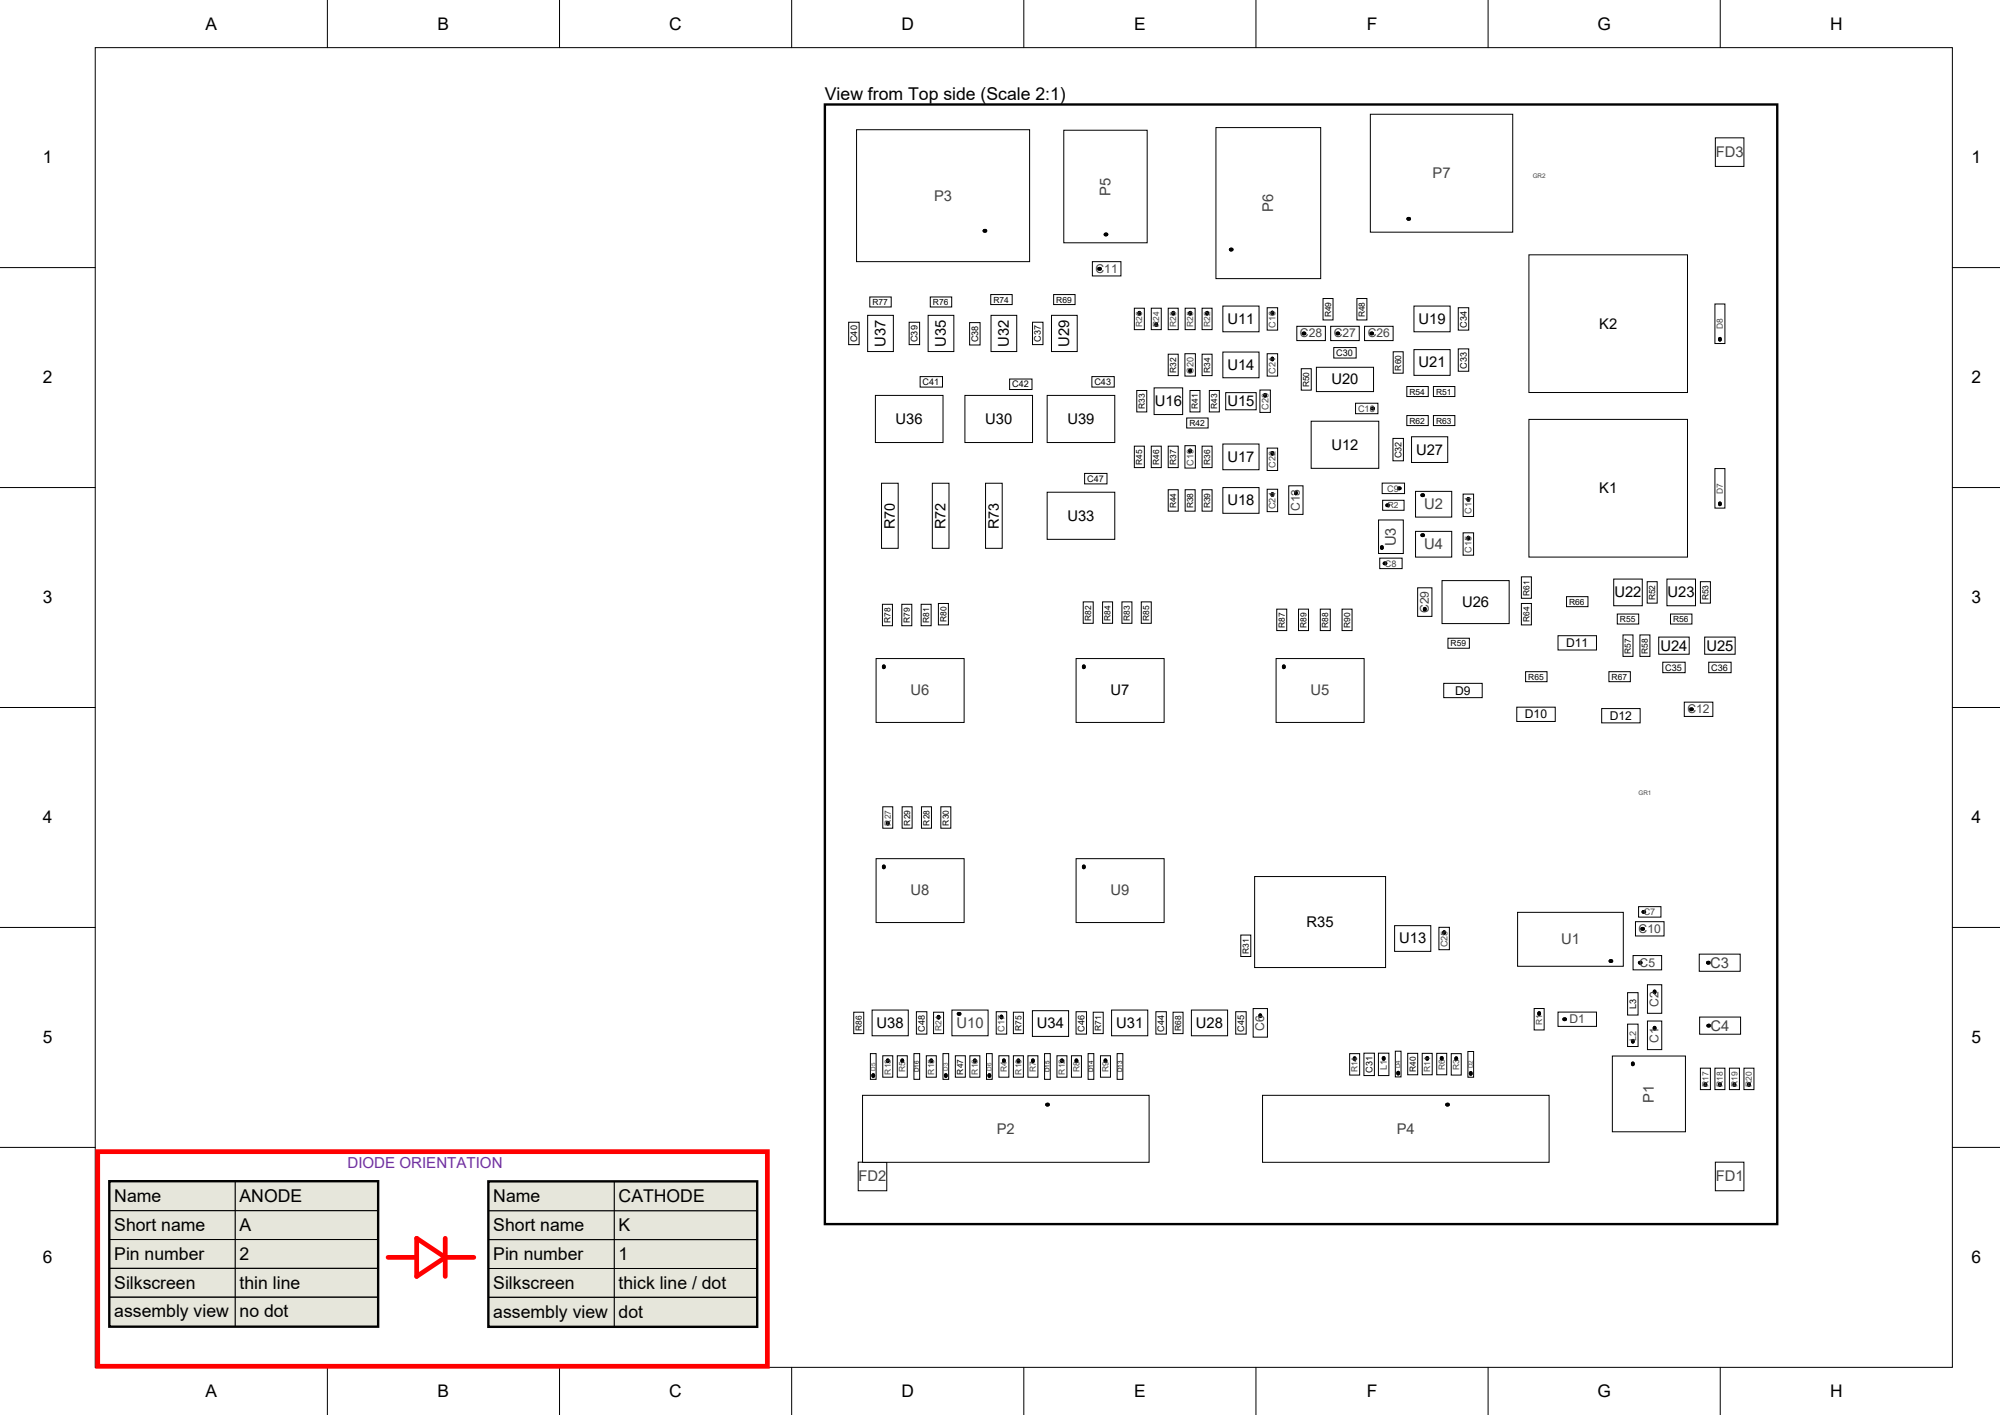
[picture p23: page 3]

View from Top side (Scale 2:1)

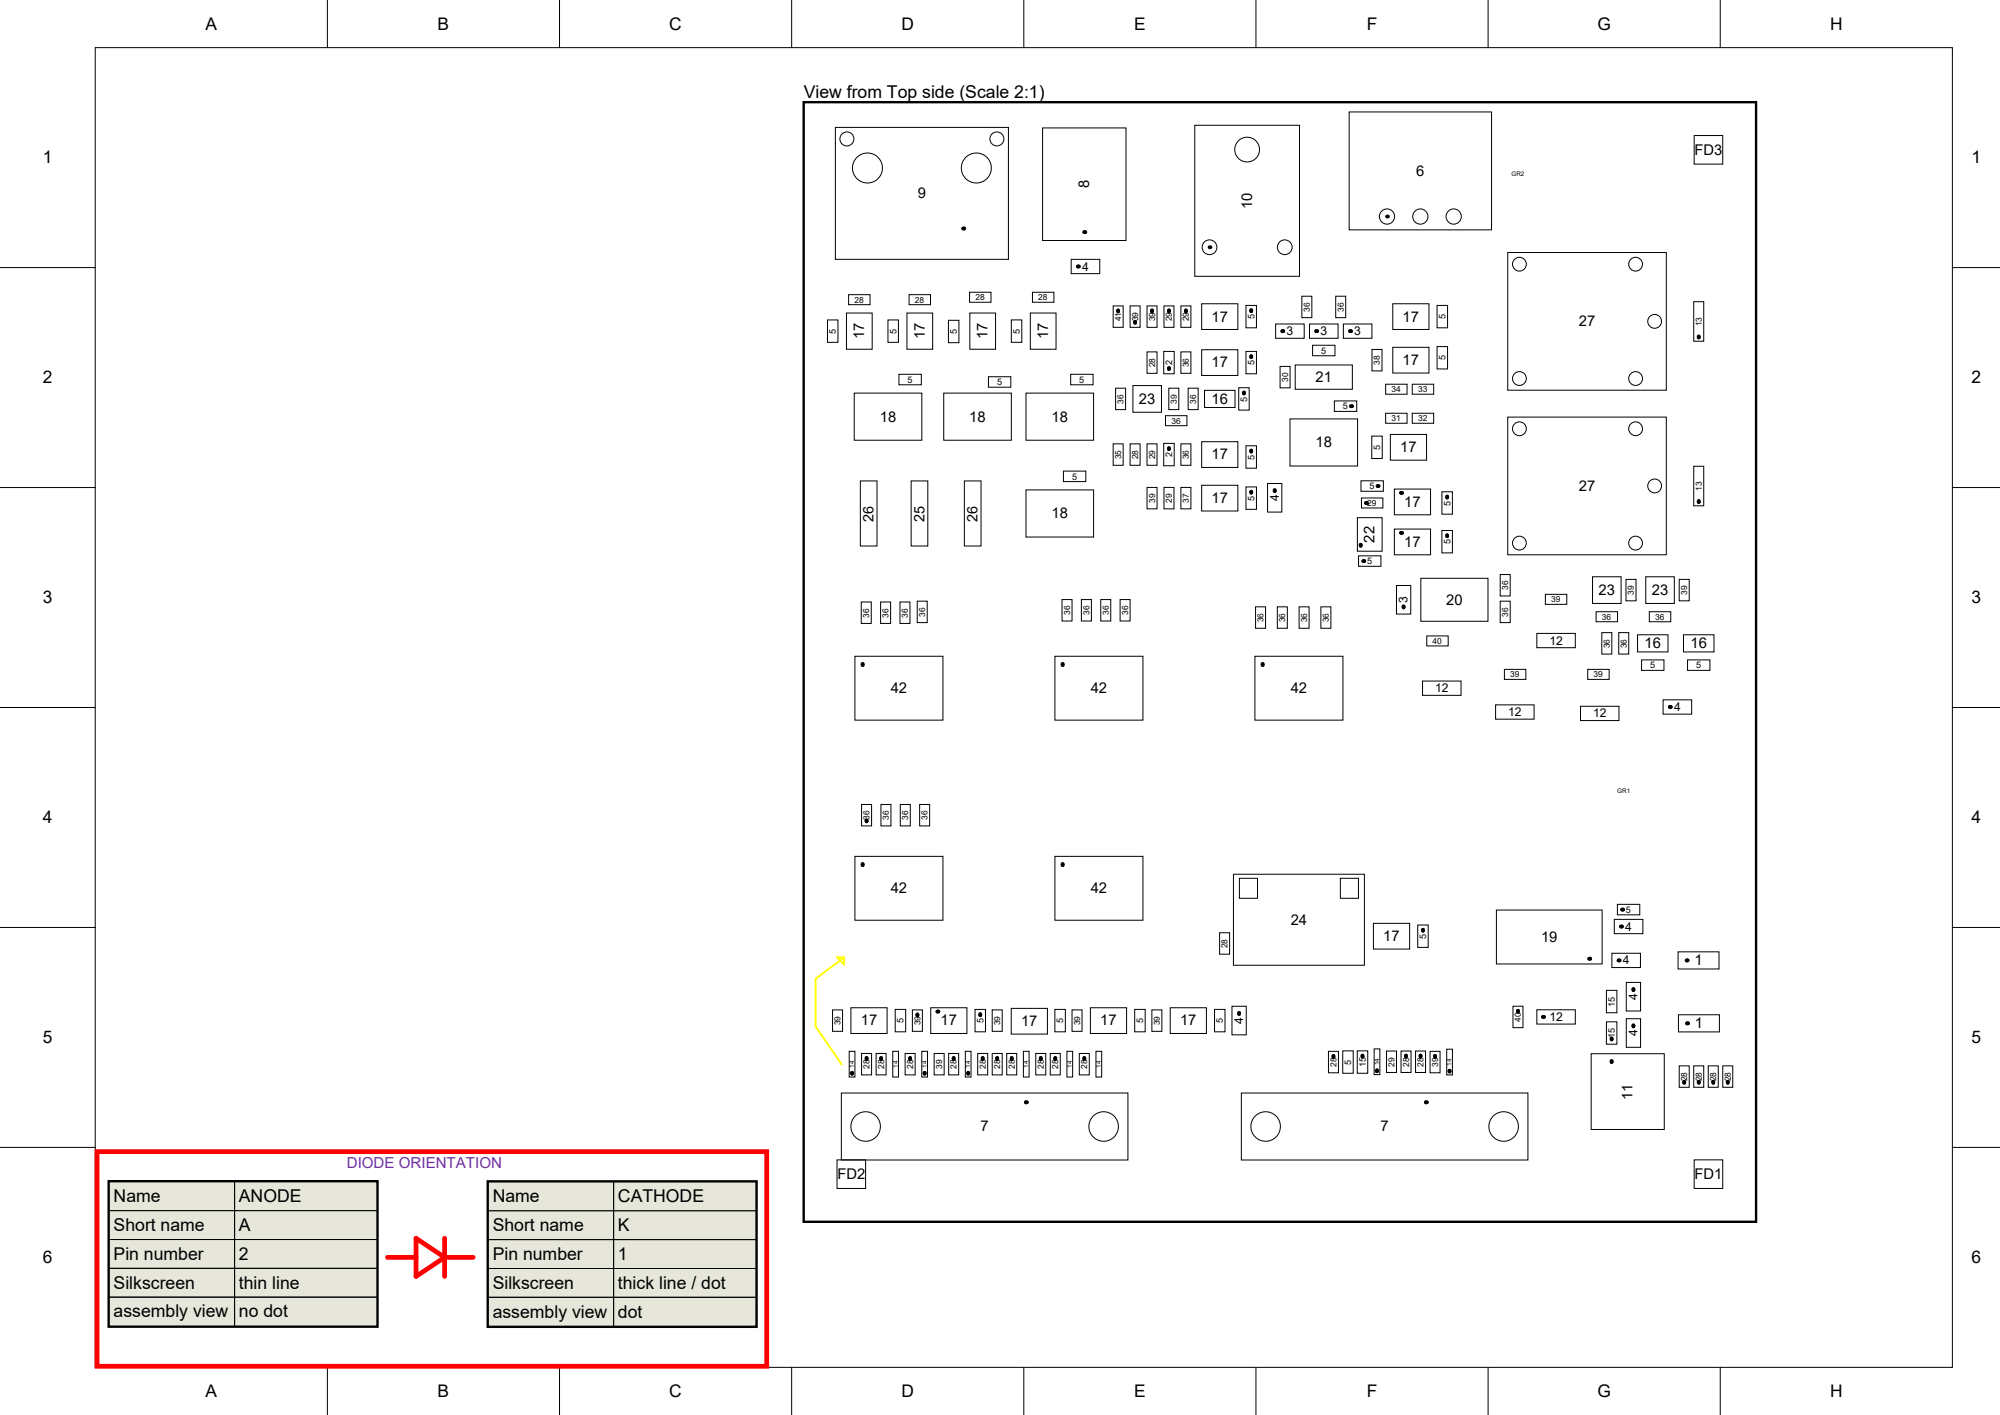
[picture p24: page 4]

View from Top side (Scale 2:1)

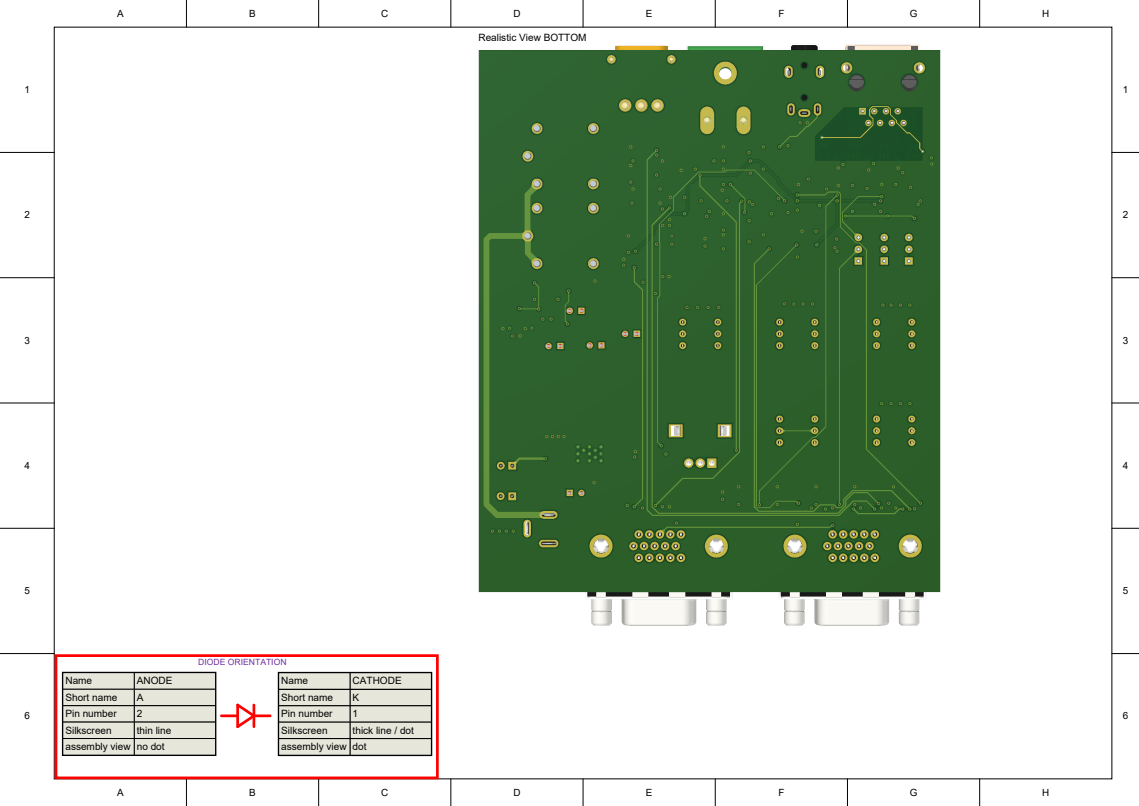
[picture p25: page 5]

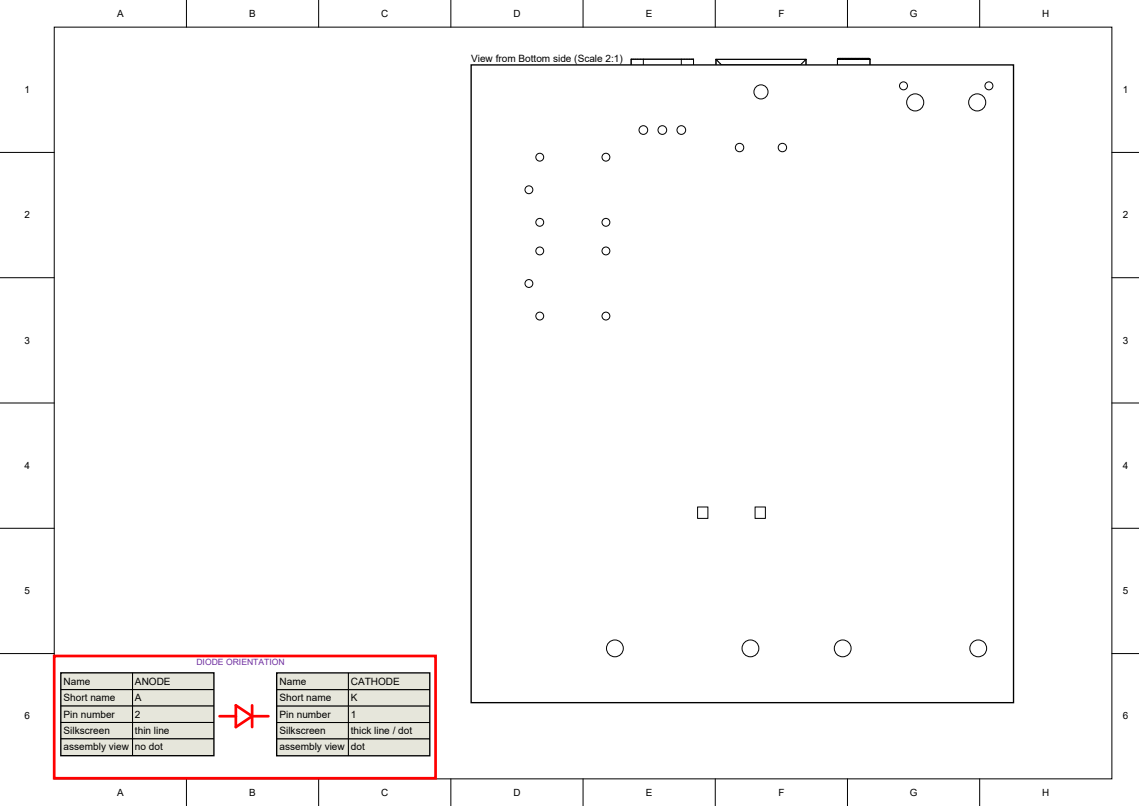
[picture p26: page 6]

View from Bottom side (Scale 2:1)

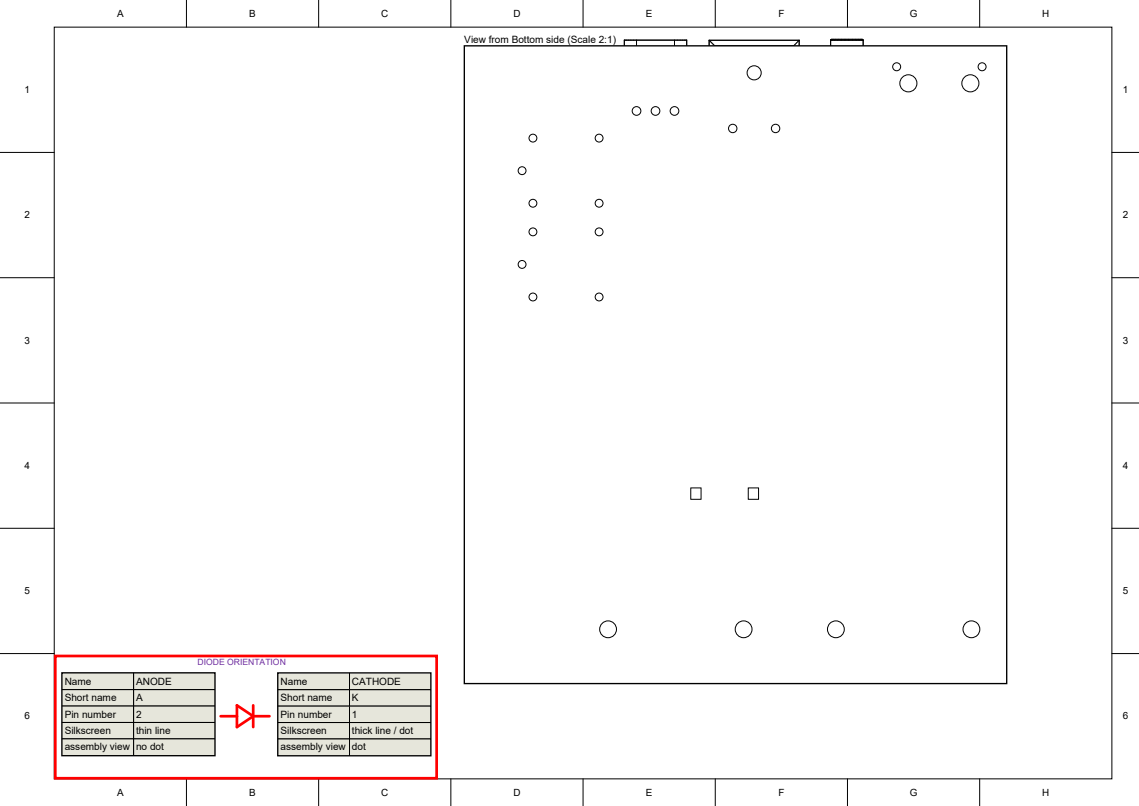
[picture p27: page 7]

View from Bottom side (Scale 2:1)

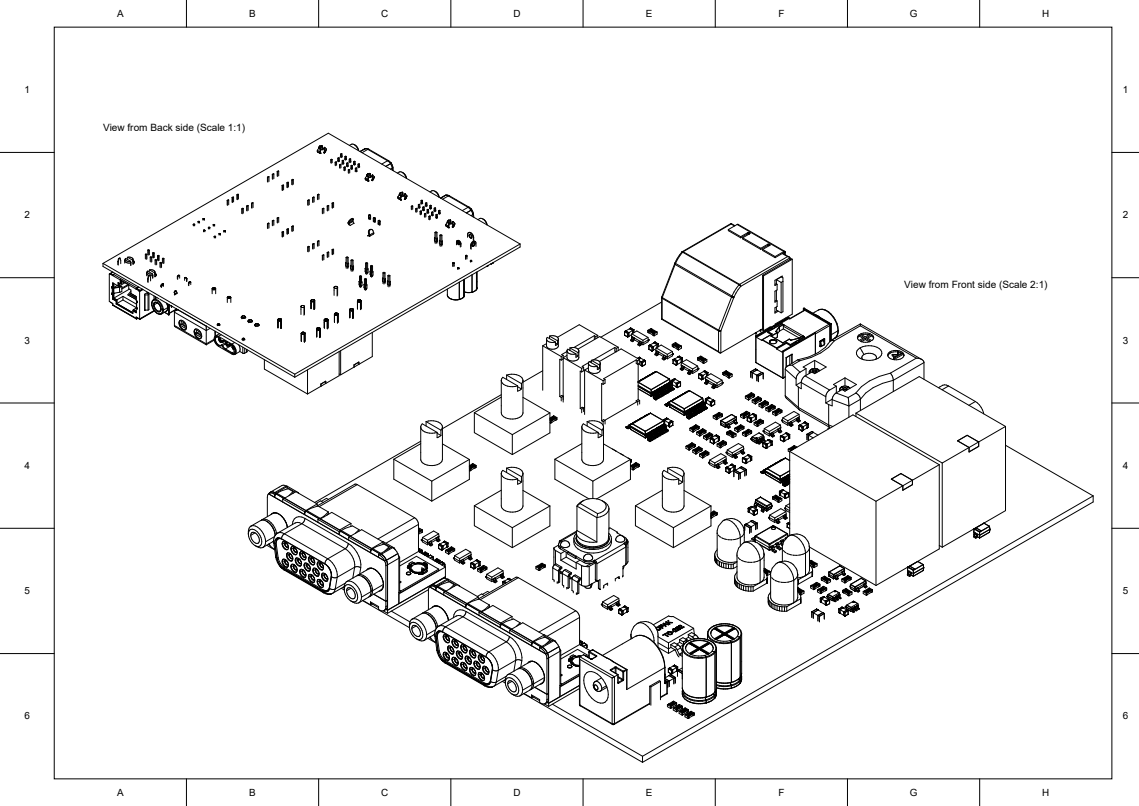
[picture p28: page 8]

View from Back side (Scale 1:1)

View from Front side (Scale 2:1)

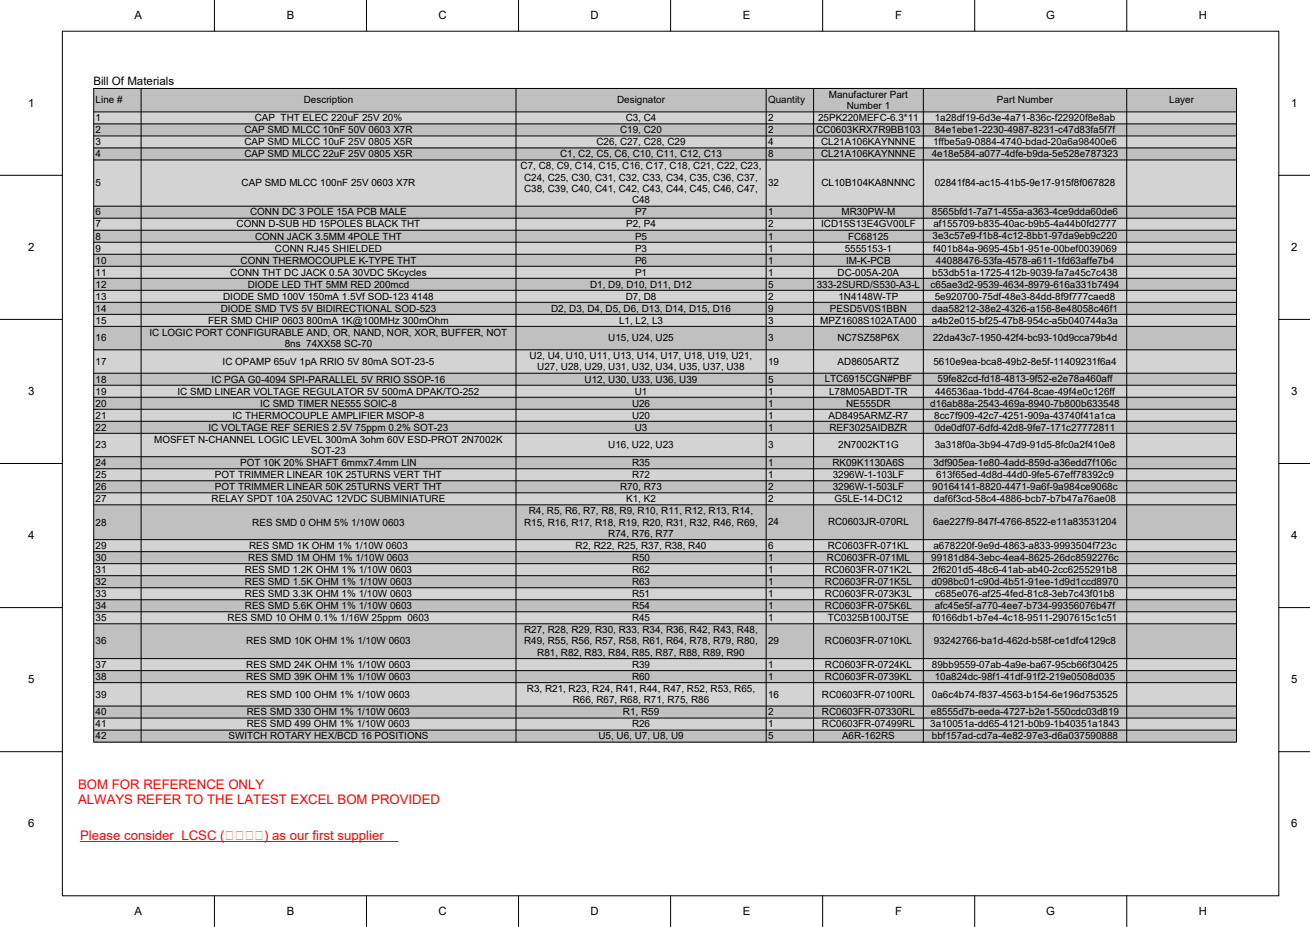
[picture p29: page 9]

Line # | Description | Designator | Quantity | Manufacturer Part Number 1 | Part Number | Layer

1 | CAP THT ELEC 220uF 25V 20% | C3, C4 | 2 | 25PK220MEFC-6.3*11 | 1a28df19-6d3e-4a71-836c-f22920f8e8ab
2 | CAP SMD MLCC 10nF 50V 0603 X7R | C19, C20 | 2 | CC0603KRX7R9BB103 | 84e1ebe1-2230-4987-8231-c47d83fa5f7f
3 | CAP SMD MLCC 10uF 25V 0805 X5R | C26, C27, C28, C29 | 4 | CL21A106KAYNNNE | 1ffbe5a9-0884-4740-bdad-20a6a98400e6
4 | CAP SMD MLCC 22uF 25V 0805 X5R | C1, C2, C5, C6, C10, C11, C12, C13 | 8 | CL21A106KAYNNNE | 4e18e584-a077-4dfe-b9da-5e528e787323
5 | CAP SMD MLCC 100nF 25V 0603 X7R | C7, C8, C9, C14, C15, C16, C17, C18, C21, C22, C23, C24, C25, C30, C31, C32, C33, C34, C35, C36, C37, C38, C39, C40, C41, C42, C43, C44, C45, C46, C47, C48 | 32 | CL10B104KA8NNNC | 02841f84-ac15-41b5-9e17-915f8f067828

6 | CONN DC 3 POLE 15A PCB MALE | P7 | 1 | MR30PW-M | 8565bfd1-7a71-455a-a363-4ce9dda60de6
7 | CONN D-SUB HD 15POLES BLACK THT | P2, P4 | 2 | ICD15S13E4GV00LF | af155709-b835-40ac-b9b5-4a44b0fd2777
8 | CONN JACK 3.5MM 4POLE THT | P5 | 1 | FC68125 | 3e3c57e9-f1b8-4c12-8bb1-97da9eb9c220
9 | CONN RJ45 SHIELDED | P3 | 1 | 5555153-1 | f401b84a-9695-45b1-951e-00bef0039069
10 | CONN THERMOCOUPLE K-TYPE THT | P6 | 1 | IM-K-PCB | 44088476-53fa-4578-a611-1fd63affe7b4
11 | CONN THT DC JACK 0.5A 30VDC 5Kcycles | P1 | 1 | DC-005A-20A | b53db51a-1725-412b-9039-fa7a45c7c438
12 | DIODE LED THT 5MM RED 200mcd | D1, D9, D10, D11, D12 | 5 | 333-2SURD/S530-A3-L | c65ae3d2-9539-4634-8979-616a331b7494
13 | DIODE SMD 100V 150mA 1.5Vf SOD-123 4148 | D7, D8 | 2 | 1N4148W-TP | 5e920700-75df-48e3-84dd-8f9f777caed8
14 | DIODE SMD TVS 5V BIDIRECTIONAL SOD-523 | D2, D3, D4, D5, D6, D13, D14, D15, D16 | 9 | PESD5V0S1BBN | daa58212-38e2-4326-a156-8e48058c46f1
15 | FER SMD CHIP 0603 800mA 1K@100MHz 300mOhm | L1, L2, L3 | 3 | MPZ1608S102ATA00 | a4b2e015-bf25-47b8-954c-a5b040744a3a
16 | IC LOGIC PORT CONFIGURABLE AND, OR, NAND, NOR, XOR, BUFFER, NOT 8ns 74XX58 SC-70 | U15, U24, U25 | 3 | NC7SZ58P6X | 22da43c7-1950-42f4-bc93-10d9cca79b4d

17 | IC OPAMP 65uV 1pA RRIO 5V 80mA SOT-23-5 | U2, U4, U10, U11, U13, U14, U17, U18, U19, U21, U27, U28, U29, U31, U32, U34, U35, U37, U38 | 19 | AD8605ARTZ | 5610e9ea-bca8-49b2-8e5f-11409231f6a4

18 | IC PGA G0-4094 SPI-PARALLEL 5V RRIO SSOP-16 | U12, U30, U33, U36, U39 | 5 | LTC6915CGN#PBF | 59fe82cd-fd18-4813-9f52-e2e78a460aff
19 | IC SMD LINEAR VOLTAGE REGULATOR 5V 500mA DPAK/TO-252 | U1 | 1 | L78M05ABDT-TR | 446536aa-1bdd-4764-8cae-49f4e0c126ff
20 | IC SMD TIMER NE555 SOIC-8 | U26 | 1 | NE555DR | d16ab88a-2543-469a-8940-7b800b633548
21 | IC THERMOCOUPLE AMPLIFIER MSOP-8 | U20 | 1 | AD8495ARMZ-R7 | 8cc7f909-42c7-4251-909a-43740f41a1ca
22 | IC VOLTAGE REF SERIES 2.5V 75ppm 0.2% SOT-23 | U3 | 1 | REF3025AIDBZR | 0de0df07-6dfd-42d8-9fe7-171c27772811
23 | MOSFET N-CHANNEL LOGIC LEVEL 300mA 3ohm 60V ESD-PROT 2N7002K SOT-23 | U16, U22, U23 | 3 | 2N7002KT1G | 3a318f0a-3b94-47d9-91d5-8fc0a2f410e8

24 | POT 10K 20% SHAFT 6mmx7.4mm LIN | R35 | 1 | RK09K1130A6S | 3df905ea-1e80-4add-859d-a36edd7f106c
25 | POT TRIMMER LINEAR 10K 25TURNS VERT THT | R72 | 1 | 3296W-1-103LF | 613f65ed-4d8d-44d0-9fe5-67eff78392c9
26 | POT TRIMMER LINEAR 50K 25TURNS VERT THT | R70, R73 | 2 | 3296W-1-503LF | 90164141-8820-4471-9a6f-9a984ce9068c
27 | RELAY SPDT 10A 250VAC 12VDC SUBMINIATURE | K1, K2 | 2 | G5LE-14-DC12 | daf6f3cd-58c4-4886-bcb7-b7b47a76ae08
28 | RES SMD 0 OHM 5% 1/10W 0603 | R4, R5, R6, R7, R8, R9, R10, R11, R12, R13, R14, R15, R16, R17, R18, R19, R20, R31, R32, R46, R69, R74, R76, R77 | 24 | RC0603JR-070RL | 6ae227f9-847f-4766-8522-e11a83531204
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

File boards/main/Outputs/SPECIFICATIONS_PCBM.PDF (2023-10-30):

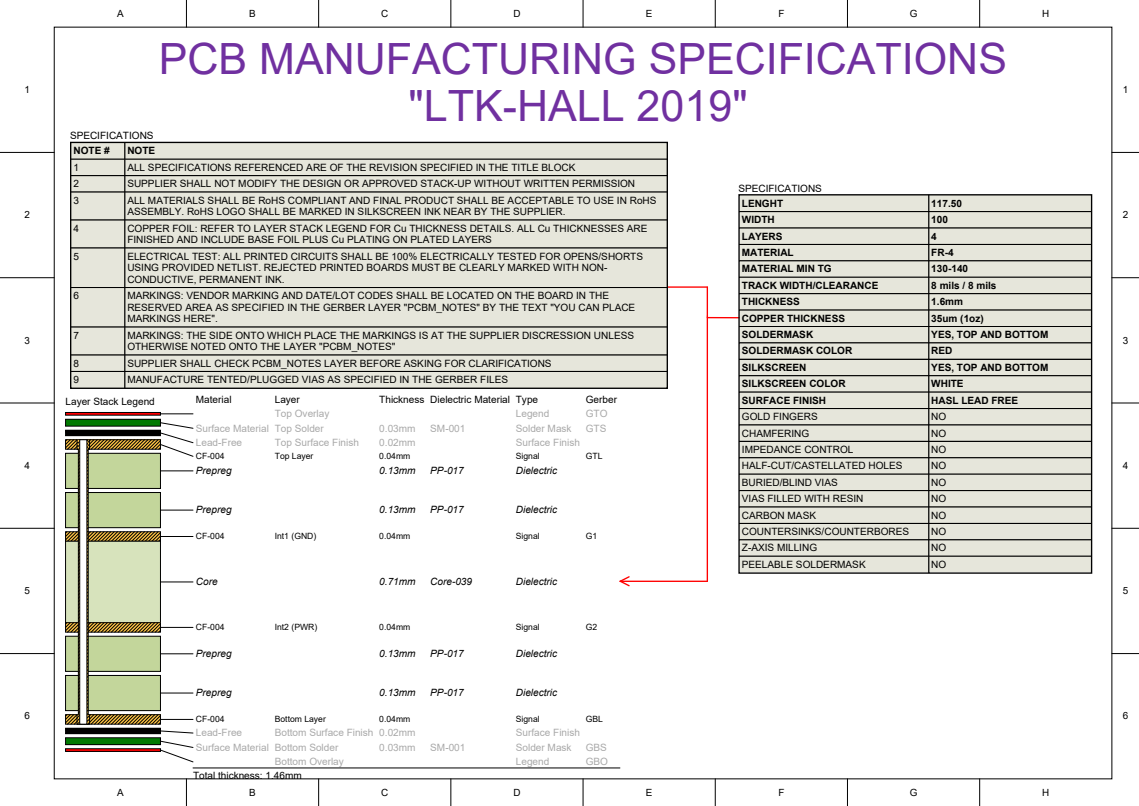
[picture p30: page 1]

NOTE # | NOTE
1 | ALL SPECIFICATIONS REFERENCED ARE OF THE REVISION SPECIFIED IN THE TITLE BLOCK
2 | SUPPLIER SHALL NOT MODIFY THE DESIGN OR APPROVED STACK-UP WITHOUT WRITTEN PERMISSION
3 | ALL MATERIALS SHALL BE RoHS COMPLIANT AND FINAL PRODUCT SHALL BE ACCEPTABLE TO USE IN RoHS ASSEMBLY. RoHS LOGO SHALL BE MARKED IN SILKSCREEN INK NEAR BY THE SUPPLIER.

LENGHT | 117.50
WIDTH | 100
LAYERS | 4
MATERIAL | FR-4
MATERIAL MIN TG | 130-140
TRACK WIDTH/CLEARANCE | 8 mils / 8 mils
THICKNESS | 1.6mm
COPPER THICKNESS | 35um (1oz)

4 | COPPER FOIL: REFER TO LAYER STACK LEGEND FOR Cu THICKNESS DETAILS. ALL Cu THICKNESSES ARE FINISHED AND INCLUDE BASE FOIL PLUS Cu PLATING ON PLATED LAYERS

5 | ELECTRICAL TEST: ALL PRINTED CIRCUITS SHALL BE 100% ELECTRICALLY TESTED FOR OPENS/SHORTS USING PROVIDED NETLIST. REJECTED PRINTED BOARDS MUST BE CLEARLY MARKED WITH NON-CONDUCTIVE, PERMANENT INK.

6 | MARKINGS: VENDOR MARKING AND DATE/LOT CODES SHALL BE LOCATED ON THE BOARD IN THE RESERVED AREA AS SPECIFIED IN THE GERBER LAYER "PCBM_NOTES" BY THE TEXT "YOU CAN PLACE MARKINGS HERE".

MARKINGS: THE SIDE ONTO WHICH PLACE THE MARKINGS IS AT THE SUPPLIER DISCRESSION UNLESS
OTHERWISE NOTED ONTO THE LAYER "PCBM_NOTES"

YES, TOP AND BOTTOM

SOLDERMASK COLOR | RED
SILKSCREEN | YES, TOP AND BOTTOM
SILKSCREEN COLOR | WHITE
SURFACE FINISH | HASL LEAD FREE
GOLD FINGERS | NO
CHAMFERING | NO
IMPEDANCE CONTROL | NO
HALF-CUT/CASTELLATED HOLES | NO
BURIED/BLIND VIAS | NO
VIAS FILLED WITH RESIN | NO
CARBON MASK | NO
COUNTERSINKS/COUNTERBORES | NO
Z-AXIS MILLING | NO
PEELABLE SOLDERMASK | NO

8 | SUPPLIER SHALL CHECK PCBM_NOTES LAYER BEFORE ASKING FOR CLARIFICATIONS
9 | MANUFACTURE TENTED/PLUGGED VIAS AS SPECIFIED IN THE GERBER FILES

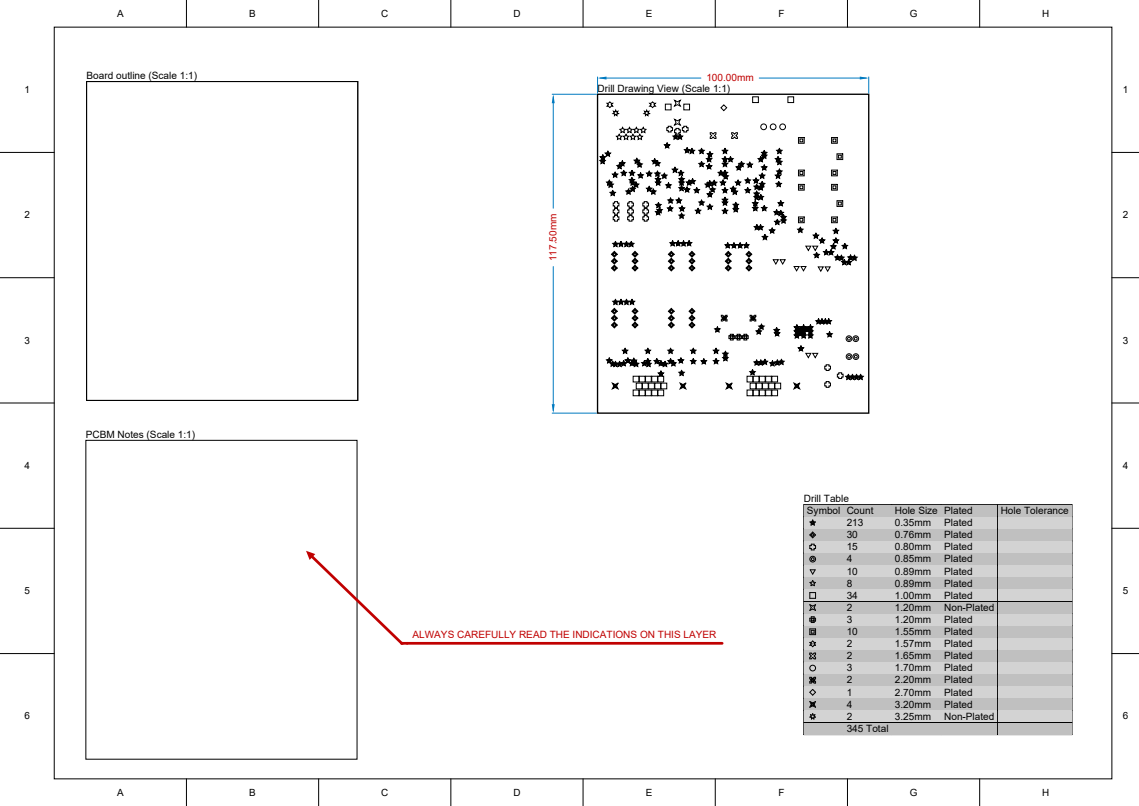
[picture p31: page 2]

Drill Drawing View (Scale 1:1)

ALWAYS CAREFULLY READ THE INDICATIONS ON THIS LAYER 117.50mm

Symbol | Count | Hole Size | Plated | Hole Tolerance

213 | 0.35mm | Plated
30 | 0.76mm | Plated
15 | 0.80mm | Plated
4 | 0.85mm | Plated
10 | 0.89mm | Plated
8 | 0.89mm | Plated
34 | 1.00mm | Plated
2 | 1.20mm | Non-Plated
3 | 1.20mm | Plated
10 | 1.55mm | Plated
2 | 1.57mm | Plated
2 | 1.65mm | Plated
3 | 1.70mm | Plated
2 | 2.20mm | Plated
1 | 2.70mm | Plated
4 | 3.20mm | Plated
2 | 3.25mm | Non-Plated
345 Total

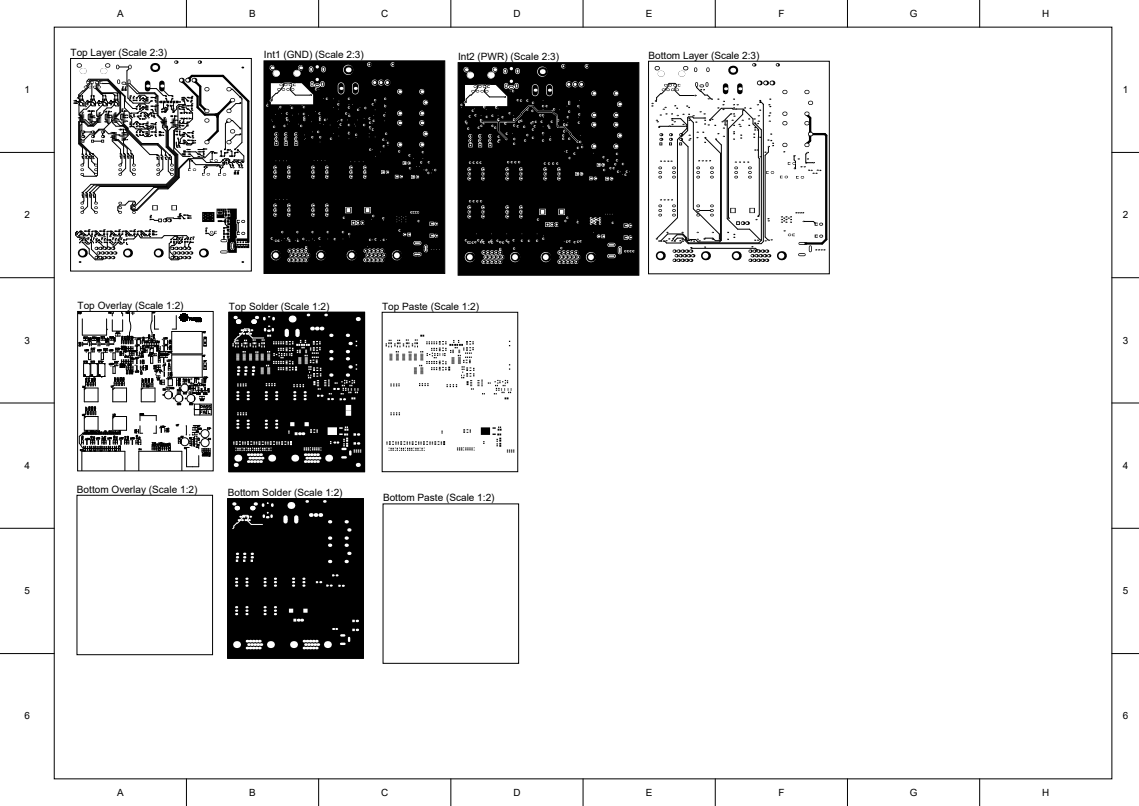
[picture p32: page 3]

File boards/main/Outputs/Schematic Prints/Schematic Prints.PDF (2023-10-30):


D0 | 1
D1 | 2
D2 | 4

SAMPLE_VH2_P
SAMPLE_VH2_N
SAMPLE_I_P

C:\Users\Shadow\Desktop\Repos\ltk-hall-electronics\boards\main\ltk-hall_main.SchDoc


DIN(D1) 7
CLK(D2) 8
DOUT(D3) 9

HOLD_THRU 5
PAR_SER 11

C:\Users\Shadow\Desktop\Repos\ltk-hall-electronics\boards\main\ltk-hall_main_gauss.SchDoc


+5 | VCC 5

OR AS SCHMITT BUFFER GND

C:\Users\Shadow\Desktop\Repos\ltk-hall-electronics\boards\main\ltk-hall_main_igen.SchDoc


COMPARATOR WITH HYSTERESIS
OUTPUT ACTIVE LOW
SET WITH T=150°C (3.25V) (OUT LOW)
RESET WITH T=100°C (3V) (OUT HIGH)

C:\Users\Shadow\Desktop\Repos\ltk-hall-electronics\boards\main\ltk-hall_main_tc_heater.SchDoc


PAR_SER 11

R73 | | DIN(D1) 7
50K 25t | | CLK(D2) 8

DOUT(D3) 9

DIN(D1) 7

C:\Users\Shadow\Desktop\Repos\ltk-hall-electronics\boards\main\ltk-hall_main_vh.SchDoc


DIN(D1) 7
CLK(D2) 8
DOUT(D3) 9

HOLD_THRU 5
PAR_SER 11

C:\Users\Shadow\Desktop\Repos\ltk-hall-electronics\boards\main\ltk-hall_main_vr.SchDoc

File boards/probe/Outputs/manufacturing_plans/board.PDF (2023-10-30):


View from Left side (Scale 2:1)

View from Front side (Scale 2:1)

View from Right side (Scale 2:1)

View from Left side (Scale 1:1)

View from Top side (Scale 1:1)

Hall Effect, Probe board


Drill Drawing View (Scale 2:1)

Symbol | Count | Hole Size | Plated | Hole Tolerance

2 | 0.70mm | Plated
2 | 0.75mm | Plated
2 | 1.20mm | Plated
2 | 0.80mm | Plated
3 | 0.60mm | Plated
11 Total

NAME | SIGNATURE | DATE | NOTES | TITLE:

DRAW | Davide Bortolami | | | | Hall Effect, Probe board
CHK'D | Davide Bortolami

APPV'D | Davide Bortolami
MFG | ND
QA | | | | | Fermium LABS srl Via Monselice 15a 35142 Padova PD Italy | info@fermiumlabs.com https://fermiumlabs.com +39 049 736-0954 VAT: IT04986880286 | SIZE

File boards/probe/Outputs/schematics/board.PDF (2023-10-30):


Size: A4 | Number: 1 | Revision: *
Date: 10/30/2023 Time: 4:41:26 PM | | Sheet 1 of | Italy 1

Fermium LABS logo

C:\Users\Shadow\Desktop\Repos\ltk-hall-electronics\boards\probe\probe.SchDoc

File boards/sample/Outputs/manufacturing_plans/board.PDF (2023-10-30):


View from Front side (Scale 2:1)

View from Top side (Scale 2:1)

View from Back side (Scale 2:1)

View from Top side (Scale 1:1)

Hall Effect, Sample board


Symbol | Count | Hole Size | Plated | Hole Tolerance

23 | 0.76mm | Plated
1 | 1.00mm | Plated
4 | 1.27mm | Plated
2 | 2.70mm | Plated
30 Total

NAME | SIGNATURE | DATE | NOTES | TITLE:

DRAW | Davide Bortolami | | | | Hall Effect, Sample board
CHK'D | Davide Bortolami

APPV'D | Davide Bortolami
MFG | ND
QA | | | | | Fermium LABS srl Via Monselice 15a 35142 Padova PD Italy | info@fermiumlabs.com https://fermiumlabs.com +39 049 736-0954 VAT: IT04986880286 | SIZE

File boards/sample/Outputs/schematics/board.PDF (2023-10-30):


SAMPLE-Vr_P
SAMPLE-Vr_N
SAMPLE-VH1_P
SAMPLE-VH1_N
SAMPLE-VH2_P

When sourcing the Germanium, ask for
"ingot" not "wafer", it implies a less
expensive procedure to cut and no
un-needed qualities.

Size: A4 | Number: 1 | Revision: *
Date: 10/30/2023 Time: 4:43:03 PM | | Sheet 1 of | Italy 1

Fermium LABS logo

C:\Users\Shadow\Desktop\Repos\ltk-hall-electronics\boards\sample\sample_board.SchDoc

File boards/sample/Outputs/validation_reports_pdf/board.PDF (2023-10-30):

## Electrical Rules Check Report

Class | Document | Message
Warning | sample_board.SchDoc | Nets Wire SAMPLE-VH1_P has multiple names (Net Label SAMPLE-VH1_P, Net Labe
| | SAMPLE-VH2_P)
Warning | sample_board.SchDoc | Off grid Net Label SAMPLE-I_P at 4841.509mil,4150mil
Warning | sample_board.SchDoc | Off grid Net Label SAMPLE-VH1_P at 4696.006mil,4550mi
Warning | sample_board.SchDoc | Off grid Net Label SAMPLE-VH2_N at 4678.671mil,4250mi
Warning | sample_board.SchDoc | Off grid Net Label SAMPLE-Vr_N at 4758.962mil,4650mi
Warning | sample_board.SchDoc | Off grid Net Label SAMPLE-Vr_P at 4776.297mil,4750mi
Monday 30 Oct 2023 4:42:45 PM | Page 1 of 1


Design Rules Verification Report

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

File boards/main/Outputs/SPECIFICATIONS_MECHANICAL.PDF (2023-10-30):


View from Front side (Scale 2:1)


View from Top side (Scale 1:1)

View from Front side (Scale 1:1)

View from Back side (Scale 1:1)

View from Bottom side (Scale 1:1)

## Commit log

2016-10-05 fix directory and filenames, directory structure
    [main_board.PrjPcb, sample_board.PrjPcb]
2016-10-05 fixed sample board pcb project
    [sample_board.PrjPcb]
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2016-10-20 fix issue #5
    [main_board.SchDoc]
2016-10-20 fixed issue #10
    [hub_board.SchDoc, main_board.SchDoc]
2016-10-20 Ignore a few files and fix issue #3 Deleted ground planes in the main board
    [main_board.PcbDoc, main_board.SchDoc]
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2016-10-20 supposedly fixed #12
    [main_board.SchDoc]
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2016-10-20 fixed #14
    [main_board.SchDoc]
2016-10-20 addressing issue #11
    [hub_board.PcbDoc, hub_board.SchDoc]
2016-10-20 fixed #17
    [hub_board.SchDoc, main_board.SchDoc, sample_board.SchDoc]
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2016-10-24 added libraries changed atmega: fixed #21
    [main_board.SchDoc]
2016-10-24 fixed #7, added the required capacitors
    [main_board.SchDoc]
2016-10-24 fixed #23
    [main_board.SchDoc]
2016-10-24 moved free pin in the ethernet connector j1 from 3 to 6 in both main and hub boards added pullup resistors to those pins "3" in the main board, and connected them to gnd in the hub board. Connected t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
    [hub_board.SchDoc, main_board.SchDoc]
2016-11-04 Cleaned up, removed balancing potetiometer. Fixed issue when schotty diodes would clamp up the Vres value because it was before the voltage divider.
    [main_board.SchDoc]
2016-11-04 removed banana connectos as per issue #16
    [main_board.SchDoc]
2016-11-04 Small fixes and cleanuos
    [main_board.SchDoc]
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2016-11-07 Various small fixes to nets
    [main_board.SchDoc]
2016-11-07 fixed #28
    [hub_board.SchDoc]
2016-11-07 New Germanium sample simplified footprint New 8-pin widened connector for sample Removed unusued holes Removed thermocouple traces Removed Pin names Small fixes and cleanups to the sample board
    [sample_board.PcbDoc, sample_board.SchDoc]
2016-11-08 New hub board schematic with reduced component count, withouth the opamp. Various fixes to hub board schematic
    [hub_board.SchDoc]
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2016-11-09 Changed ADC as per issue #15
    [main_board.SchDoc]
2016-11-10 Cleaned up schotty diodes schematic New connector on both hub and main board, more compact and easier to make Cleaned up adc schematics Added adc pullup resistors for i2c lines Renamed thermocouple o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
    [hub_board.SchDoc, main_board.SchDoc]
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2016-11-22 fixes and improvements
    [hub_board.SchDoc, main_board.SchDoc, sample_board.PcbDoc]
2016-11-23 Added MAX5805 adc imported from ultralibrarian software, regarding issue #8
    [main_board.PrjPcb, main_board.SchDoc]
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2016-11-28 Fixed comments and values on ALLLLLLL COMPONENTS
    [bncs.SchDoc, hub_board.SchDoc, mcu.SchDoc, power_supply.SchDoc]
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2016-11-28 Correct footprints for ALL DIODES and ALL CAPACITORS
    [cc_gen_and_heat_pwr.SchDoc, hub_board.PrjPcb, hub_board.SchDoc, main_board.PrjPcb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]
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2016-11-30 fixed many issues
    [hub_board.PrjPcb, hub_board.SchDoc, mcu.SchDoc]
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2016-11-30 New footprint for optoisolator, fix various problems
    [cc_gen_and_heat_pwr.SchDoc, mcu.SchDoc]
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2016-12-01 fixed many many footprints and supplier data
    [bncs.SchDoc, cables.SchDoc, main_board.PrjPcb, mcu.SchDoc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]
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2016-12-02 Changed 15v nets to 12v nets, added a third (third!) adc, fixed issues, started main board with imported cad drawing
    [bncs.SchDoc, hub_board.PrjPcb, hub_board.SchDoc, main_board.PcbDoc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]
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2016-12-02 Fixed annotation to accomodate the new 2.5v circuit
    [bncs.SchDoc, mcu.SchDoc, power_supply.SchDoc]
2016-12-02 Found the toroidal transformer! fixed #37
    [main_board.PrjPcb, power_supply.SchDoc]
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2016-12-04 correct board shape designed in autocad
    [G735V with profile.dwg, main_board.PcbDoc]
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2016-12-07 Choosed remaining components, updated BOM, fixed missing ones, new pcb connectors
    [power_supply.SchDoc]
2016-12-07 fixed problem with enclosure 3d file
    [main_board.PcbDoc]
2016-12-09 Fixed component footprint, routed partly the main board, various fixes
    [bncs.SchDoc, main_board.PcbDoc, main_board.PrjPcb, mcu.SchDoc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]
2016-12-09 Revert "fixed problem with enclosure 3d file"
    This reverts commit 5bbb327dd36eff3501d6cb2a6dc13ba61b68ca57.
    [main_board.PcbDoc]
2016-12-09 Revert "Choosed remaining components, updated BOM, fixed missing ones, new pcb connectors"
    This reverts commit 28de5c2b345b3faba05a83d6833d71e794ccd0a5.
    [power_supply.SchDoc]
2016-12-13 Added new drawing and new components. Work in progress. Fixed #38. Fixed #40. Working on #41.
    [main_board.PcbDoc, power_supply.SchDoc]
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2016-12-16 fix and merge latest changes
    [main_board.PcbDoc, main_board.PrjPcb, power_supply.SchDoc]
2016-12-16 Routed more partf of the PCB, fixed some components
    [main_board.PcbDoc, main_board.PrjPcb, power_supply.SchDoc]
2016-12-19 Many many project fixes
    [hub_board.PrjPcb, main_board.PcbDoc, main_board.PrjPcb, mcu.SchDoc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]
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2016-12-24 RJ45GE 3d body, improvement and fixes to hub board
    [hub_board.PcbDoc, hub_board.PrjPcb, hub_board.SchDoc]
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2017-01-06 Some updates and fixes to the project as a whole
    [hub_board.PcbDoc, hub_board.PrjPcb, hub_board.SchDoc]
2017-01-06 some other fixes
    [hub_board.SchDoc]
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2017-01-14 last fix to the DC connector in the hub board. May you rest in peace till manufacturing
    [hub_board.PcbDoc]
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2017-02-05 Added draftsman document for main board, another few hours of work on the main board. Fixed nets name in bncs.schdoc.
    [bncs.SchDoc, main_board.PcbDoc, main_board.PrjPcb, mcu.SchDoc]
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2017-02-26 Added BOM info to components in the new current generator. Fixed bug with the output voltage of two differential amplifiers. Added two buffer opamps to the 2.5V reference to allow current sinking and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
    [cc_gen_and_heat_pwr.SchDoc, hub_board.SchDoc, main_board.PrjPcb, mcu.SchDoc]
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2017-02-27 Fixed #48, worked on #43, Fixed #44, Worked on #46
    [cc_gen_and_heat_pwr.SchDoc, hub_board.PcbDoc, hub_board.PrjPcb, hub_board.SchDoc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]
2017-02-27 Added output job for the probe, added draftsman document for the sample board. Fixes to bomdocs, schematics etc etc
    [cc_gen_and_heat_pwr.SchDoc, main_board.PrjPcb, probe.PcbDoc, sample_board.PrjPcb]
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2017-02-28 Fixed a few issues. Added cables assemblies. Fixed #50
    [assemblies.SchDoc, cc_gen_and_heat_pwr.SchDoc, hub_board.PcbDoc, hub_board.PrjPcb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]
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2017-03-02 Now main board sch-->pcb import design changes works like a charm. Also partial routing of the new power supply schematic. Fixes to footprints and missing libraries.
    [main_board.PcbDoc, main_board.PrjPcb, power_supply.SchDoc]
2017-03-02 heatsink footprint. routing routing routing again. Fixed wrong nets in the bncs.SchDoc, which reminds me i have to seriously design the schematic interconnect the right way!
    [bncs.SchDoc, cc_gen_and_heat_pwr.SchDoc, main_board.PcbDoc]
2017-03-03 Reorganizing main board layout. Small fixes to hub board
    [bncs.SchDoc, hub_board.PcbDoc, hub_board.SchDoc, main_board.PcbDoc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]
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2017-03-08 crunching errors one by one. Perchè altium fa le bizze?
    [cc_gen_and_heat_pwr.SchDoc, main_board.PrjPcb]
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2017-03-09 fixed various rules, various problems. Please refer to hub board for rules.
    [hub_board.PcbDoc, hub_board.PrjPcb, probe.PcbDoc, probe.PrjPcb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]
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2017-03-10 fixing problems
    [hub_board.PcbDoc]
2017-03-10 fixing problems fixing problems fixing problems
    [cc_gen_and_heat_pwr.SchDoc, main_board.PrjPcb, main_board.SchDoc, mcu.SchDoc]
2017-03-10 complete schematic refactor underway. Still problems moving changes to the main board
    [bncs.SchDoc, cc_gen_and_heat_pwr.SchDoc, main_board.PrjPcb, main_board.SchDoc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]
2017-03-10 solved all the problems after the schematic refractoring
    [bncs.SchDoc, cc_gen_and_heat_pwr.SchDoc, main_board.PrjPcb, main_board.SchDoc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]
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2017-03-10 all rules and problems on pcbs fixed, apparently
    [hub_board.PcbDoc, probe.PcbDoc, probe.SchDoc]
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2017-03-12 save before addressing a quintillion of issues
    [sample_board.PrjPcb]
2017-03-12 fixed #108
    [voltage_ref.SchDoc]
2017-03-12 fixed #107
    [instr_amp.SchDoc]
2017-03-12 trying to fix problems in the probe draftsman
    [gaussmeter_and_temp.SchDoc, probe.PcbDoc, probe.SchDoc]
2017-03-12 fixed #91
    [mcu.SchDoc, protoboard.SchDoc]
2017-03-12 fixed #94
    [main_board.SchDoc]
2017-03-12 fixed #95
    [cc_gen_and_heat_pwr.SchDoc]
2017-03-12 fixed #90 and not only
    [bncs.SchDoc]
2017-03-12 fixed #70
    [cc_gen_and_heat_pwr.SchDoc]
2017-03-12 fixed #66 and many other
    [main_board.SchDoc]
2017-03-12 fixed #100
    [sample_board.PcbDoc]
2017-03-12 fixed #71
    [main_board.SchDoc]
2017-03-12 fixed #80
    [assemblies.SchDoc, bncs.SchDoc, cc_gen_and_heat_pwr.SchDoc, db25.SchDoc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]
2017-03-12 fixed #61
    [hub_board.PcbDoc, hub_board.SchDoc]
2017-03-12 fixed #65
    [hub_board.PcbDoc, hub_board.SchDoc, main_board.SchDoc, probe.PcbDoc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]
2017-03-14 fixed #110
    [hub_board.PcbDoc, power_supply.SchDoc, sample_board.PcbDoc]
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2017-03-14 fixed output files
    [hub_board.PcbDoc, probe.PcbDoc, sample_board.SchDoc]
2017-03-14 too thin board outline in main board fixed
    [main_board.PrjPcb, sample_board.PrjPcb]
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
